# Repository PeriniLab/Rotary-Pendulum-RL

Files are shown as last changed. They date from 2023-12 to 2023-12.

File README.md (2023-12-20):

# Rotary-Pendulum-RL







https://github.com/PeriniM/Rotary-Pendulum-RL/assets/19621159/0168d43d-66d2-4de8-862b-840ff1d75a66

<!-- ![Rotary Pendulum](docs/assets/rotary_pybullet.jpg) -->
This is an open source project aimed at introducing people to **robotics**, from the hardware and embedded systems implementation to the software and control algorithms. The goal is to control a real life **rotary pendulum** to make it perform a swing-up and balance task.

The project is divided into four parts: **hardware**, **firmware**, **simulation** and **control**. The hardware part is responsible for the mechanical design and the electronic components. The firmware part is responsible for the embedded systems implementation. The simulation part is responsible for the simulation of the rotary pendulum in a virtual environment. The control part is responsible for the implementation of the control algorithms.

## [Documentation](https://rotary-pendulum-rl.readthedocs.io/)

## Folder Structure

```bash
├─── hardware
│   ├─── 3d_models
│   ├─── BOM
│   ├─── schematics
│   └─── instructions
│
├─── firmware
│   ├─── arduino
│   └─── platformio
│
├─── simulation
│   ├─── urdf
│   ├─── pybullet
│   └─── gazebo
│
├─── control
│   ├─── pid
│   ├─── optimal_control
│   └─── reinforcement_learning
│
└─── docs
    └─── assets
```
### 📂[hardware](hardware)

This folder contains the mechanical design and the electronic schematics as well as the instructions on how to build the rotary pendulum.
It will guide you through the process of 3D printing the parts, choosing the right mechanical and electronic components and assembling the rotary pendulum.

### 📂[firmware](firmware)

This folder contains the microcontroller code that will run on the embedded systems of the rotary pendulum.
It will guide you through the process of setting up the development environment, compiling and uploading the code to the microcontroller.

### 📂[simulation](simulation)

This folder contains the simulation code that will run on the computer. It will simulate the rotary pendulum in a virtual environment, such as the [PyBullet](https://pybullet.org/wordpress/) or [Gazebo](http://gazebosim.org/) simulators.

### 📂[control](control)

This folder contains the control code that will run on the computer. It will implement the control algorithms that will be used to control the rotary pendulum, from model-free to model-based control algorithms.

## Contributing

Contributions are what make the open source community such an amazing place to learn, inspire, and create. Any contributions you make are **greatly appreciated**.

If you want to contribute to this project, please read the [CONTRIBUTING.md](CONTRIBUTING.md) file.

## License

Distributed under the **Apache License 2.0**. See [LICENSE](LICENSE) for more information.

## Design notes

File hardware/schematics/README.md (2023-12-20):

# Schematics

The schematics of the electronics are yet to be added to the repository. The following is the drawn schematic, the pin numbers represent the GPIO pins of the ESP32 and the ones used in the code.

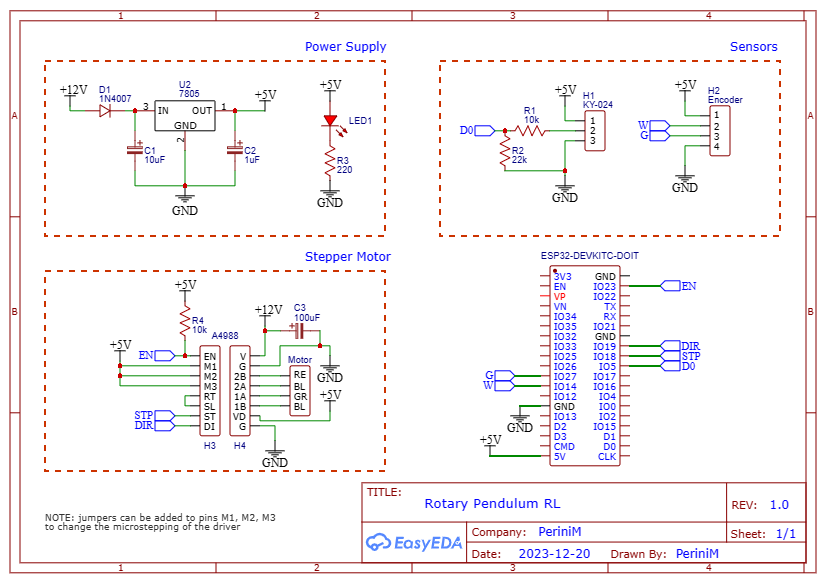
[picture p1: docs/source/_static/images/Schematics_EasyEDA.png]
Schematics


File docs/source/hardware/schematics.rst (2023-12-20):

.. _schematics:

Schematics
==========

The following is the electronics schematic to understand the connections.
Later on, a PCB will be designed.



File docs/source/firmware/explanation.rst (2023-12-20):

Example Firmware Explanation
----------------------------

The example firmware is split in three parts:

* `main.cpp` contains the main loop and the initialization code.
* `utils.cpp` contains some utility functions.
* `utils.h` contains the declarations of the utility functions.

utils.cpp
^^^^^^^^^

Here we define some utility functions that are used for handling the WiFi connection (right now it is not used) and 
for handling the pendulum rotation.
Expecially the function `getTheta` is important, since it maps the encoder counts to the angle of the pendulum.
The bar angle goes [-pi,pi] where zero is the upright position.

.. code-block:: c++

    #include <Arduino.h>
    #include <WiFi.h>
    #include <nvs_flash.h>

    bool connectToWiFi(const char* ssid, const char* password) {
    WiFi.begin(ssid, password);

    unsigned long startTime = millis();
    while (WiFi.status() != WL_CONNECTED && (millis() - startTime) < 2000) {
        delay(100);
        Serial.print(".");
    }

    if (WiFi.status() == WL_CONNECTED) {
        Serial.println("\nConnected to " + String(ssid));
        return true;
    } else {
        Serial.println("\nFailed to connect to " + String(ssid));
        WiFi.disconnect();
        return false;
    }
    }

    void setupWiFi(const char* ssids[], const char* passwords[], int NUM_NETWORKS) {
    if (nvs_flash_init() != ESP_OK) {
        Serial.println("Error initializing NVS");
        return;
    }

    nvs_handle my_handle;
    int32_t networkIndex = -1;

    if (nvs_open("storage", NVS_READONLY, &my_handle) == ESP_OK) {
        nvs_get_i32(my_handle, "networkIndex", &networkIndex);
        nvs_close(my_handle);
    }

    if (networkIndex >= 0 && networkIndex < NUM_NETWORKS) {
        if (connectToWiFi(ssids[networkIndex], passwords[networkIndex])) {
        return;
        }
    }

    for (int i = 0; i < NUM_NETWORKS; i++) {
        if (connectToWiFi(ssids[i], passwords[i])) {
        if (nvs_open("storage", NVS_READWRITE, &my_handle) == ESP_OK) {
            nvs_set_i32(my_handle, "networkIndex", i);
            nvs_commit(my_handle);
            nvs_close(my_handle);
        }
        break;
        }
    }
    }

    double getTheta(long encoderPosition, long encoderSteps) {
    double theta = 0.0;
    long half_revolutions = encoderPosition/encoderSteps; 
    if (encoderPosition > 0) {
        if (half_revolutions > 1 && half_revolutions % 2 == 0){
        theta = map(encoderPosition, half_revolutions * encoderSteps, (half_revolutions + 1)*encoderSteps, 31415,0) / 1e4;
        }
        else if (half_revolutions > 1 && half_revolutions % 2 == 1){
        theta = map(encoderPosition, half_revolutions * encoderSteps, (half_revolutions + 1)*encoderSteps, 0, -31415) / 1e4;
        }
        else {
        theta = map(encoderPosition, 0, encoderSteps, 31415, 0) / 1e4;
        }
    }
    else { 
        if (half_revolutions < -1 && half_revolutions % 2 == 0){
        theta = map(encoderPosition, half_revolutions * encoderSteps, (half_revolutions - 1)*encoderSteps, -31415,0) / 1e4;
        }
        else if (half_revolutions < -1 && half_revolutions % 2 == -1){
        theta = map(encoderPosition, half_revolutions * encoderSteps, (half_revolutions - 1)*encoderSteps, 0, 31415) / 1e4;
        }
        else {
        theta = map(encoderPosition, 0, -encoderSteps, -31415, 0) / 1e4;
        }
    }
    return theta;
    }

    double clip(double n, double lower, double upper) {
    return max(lower, min(n, upper));
    }

utils.h
^^^^^^^

Here we declare the utility functions.

.. code-block:: c++

    void setupWiFi(const char* ssids[], const char* passwords[], int NUM_NETWORKS);
    double getTheta(long encoderPosition, long encoderSteps);
    double clip(double n, double lower, double upper);

    #pragma once

main.cpp
^^^^^^^^

.. code-block:: c++

    #include <ESP32Encoder.h>
    #include <Arduino.h>
    #include "utils.h"

    // Define the pins used by the sensors
    #define ENCODER_A 14
    #define ENCODER_B 27
    #define HALL_SENSOR 26

    // Define the pins used by the stepper driver
    #define STEP_PIN 18
    #define DIR_PIN 19
    #define ENABLE_PIN 23
    // 1ULL shifts 1 to the left by STEP_PIN positions
    #define STEP_BIT (1ULL << STEP_PIN)
    #define DIR_BIT  (1ULL << DIR_PIN)
    #define ENABLE_BIT (1ULL << ENABLE_PIN)
    #define HALL_BIT (1ULL << HALL_SENSOR)

    // Define the number of networks you have
    #define NUM_NETWORKS 3

    // Create a list of SSID and passwords
    const char* ssids[NUM_NETWORKS] = {"FASTWEB-FC20AB", "ees-lab", "CasaCamilla_3"};
    const char* passwords[NUM_NETWORKS] = {"PP2NEEGH67", "cipiacelafft", "GranseolaCheSiole9102"};

    const long encoderSteps = 1200; // Encoder steps per half rotation
    ESP32Encoder encoder(true, NULL, NULL);

    const int steps_per_rev = 3200;
    // steps per second
    double maxSpeed = 4000.0; // Max speed in steps per second
    volatile double currentAngle = 0.0; // Current angle of the motor in degrees
    volatile double rangeAngle = 200.0; // Range of motion of the motor in degrees
    volatile const double degreesPerStep = 360.0 / steps_per_rev;
    volatile double speed = 0.0;
    volatile double homingSpeed = 2000.0;
    bool dir = false; // false = counter-clockwise, true = clockwise
    volatile long stepCount = 0;
    volatile bool homing = false;
    volatile bool episodeDone = false;
    volatile int hallSensorDebounce = 0;
    volatile bool hallSensorCentering = false;
    // millis variables for timing
    double timestep = 5.0; // ms
    double theta_dot = 0.0;
    double oldTheta = 0.0;
    unsigned long oldTime = 0.0;

    hw_timer_t *timer = NULL;
    portMUX_TYPE timerMux = portMUX_INITIALIZER_UNLOCKED;

    void sendSerialOutput(double angle, double angularVelocity, double currentAngle, bool episodeDone) {
    // Format the output string
    String output = String(angle) + "," + String(angularVelocity) + "," + String(currentAngle) + "," + String(episodeDone);
    Serial.println(output);
    }

    // Function to set direction
    void setDirection(bool direction) {
    dir = direction;
    if (dir) {
        GPIO.out |= DIR_BIT; // Set direction pin to HIGH
    } else {
        GPIO.out &= ~DIR_BIT; // Set direction pin to LOW
    }
    }

    // Function to set speed
    void setSpeed(double newSpeed) {
    if ((int)newSpeed == 0) {
        portENTER_CRITICAL(&timerMux);
        speed = newSpeed;
        timerAlarmDisable(timer);  // Disable the timer
        portEXIT_CRITICAL(&timerMux);
        // STEP pin to LOW to ensure the motor is not in mid-step
        GPIO.out &= ~STEP_BIT;
    } else {
        portENTER_CRITICAL(&timerMux);
        speed = newSpeed;
        timerAlarmWrite(timer, 1000000 / speed, true); // Update the timer interval
        timerAlarmEnable(timer);  // Re-enable the timer
        portEXIT_CRITICAL(&timerMux);
    }
    }

    // Function to zero the position
    void zeroPosition() {
    portENTER_CRITICAL(&timerMux);
    stepCount = 0; // Reset step count
    portEXIT_CRITICAL(&timerMux);
    }

    // Function to set speed based on percentage
    void setSpeedPercentage(int percentage) {
    speed = maxSpeed * (percentage / 100.0);
    setSpeed(speed);
    }

    // Function to move to home position
    void moveToHome() {
    homing = true;
    if (currentAngle > 0.0) {
        dir = false;
    }
    else if (currentAngle < 0.0) {
        dir = true;
    }
    else {
        homing = false;
        episodeDone = false;
        zeroPosition();
        setSpeed(0);
        return;
    }
    setDirection(dir);
    setSpeed(homingSpeed);
    }

    void IRAM_ATTR onTimer() {
    // If the speed is set to zero, exit the ISR without toggling the STEP pin
    if ((int)speed == 0) {
        return;
    }
    portENTER_CRITICAL_ISR(&timerMux);
    
    // Toggle the step pin for moving the motor
    if (GPIO.out & STEP_BIT) {
        GPIO.out &= ~STEP_BIT; // Set step pin to LOW
    } else {
        GPIO.out |= STEP_BIT; // Set step pin to HIGH
    }

    if (GPIO.in & HALL_BIT) {
        zeroPosition();
    }

    // Change steps only when step pin goes HIGH
    if (GPIO.out & STEP_BIT) {
        // update the steps the motor has moved from the beginning
        stepCount += dir ? 1 : -1;
        // convert steps to degree angle
        currentAngle = stepCount * degreesPerStep;
        // if the pendulum is not homing
        if (!homing){
        // if it is not inside the permitted range, bring pendulum back to home position
        if ((currentAngle >= rangeAngle/2 && !episodeDone) || (currentAngle <= -rangeAngle/2 && !episodeDone)) {
            episodeDone = true;
            moveToHome();
        }
        else {
            episodeDone = false;
        }
        }
        // if it is homing
        else {
        // check if the hall sensor gets activated and reset the position and speed
        if (GPIO.in & HALL_BIT && !hallSensorCentering) {
            hallSensorCentering = true;
            hallSensorDebounce = 0;
        }
        else if (GPIO.in & HALL_BIT && hallSensorCentering) {
            hallSensorDebounce++;
        }
        else if (!(GPIO.in & HALL_BIT) && hallSensorCentering && hallSensorDebounce > 5) {
            hallSensorCentering = false;
            hallSensorDebounce = 0;
            homing = false;
            episodeDone = false;
            zeroPosition();
            setSpeed(0);
            
        }
        }
    }
    
    portEXIT_CRITICAL_ISR(&timerMux);
    }

    void setup() {
    pinMode(ENCODER_A, INPUT_PULLUP);
    pinMode(ENCODER_B, INPUT_PULLUP);
    pinMode(HALL_SENSOR, INPUT);
    pinMode(ENABLE_PIN, OUTPUT);
    pinMode(STEP_PIN, OUTPUT);
    pinMode(DIR_PIN, OUTPUT);
    digitalWrite(ENABLE_PIN, LOW);  // Enable the motor

    // Connect to WiFi
    setupWiFi(ssids, passwords, NUM_NETWORKS);

    // to get accurate readings, the encoder ISR should be serviced by a core
    ESP32Encoder::isrServiceCpuCore=1;
    encoder.attachFullQuad(ENCODER_A, ENCODER_B);
    encoder.clearCount();
    encoder.setFilter(1023);

    Serial.begin(115200);

    // Set up the timer
    timer = timerBegin(0, 80, true); // Timer 0, prescaler 80, counting up
    timerAttachInterrupt(timer, &onTimer, true); // Attach onTimer function
    timerAlarmEnable(timer); // Enable the timer
    }

    void loop() {
    // get encoder count
    long currentCount = encoder.getCount();
    // map it in range [-3.14, 3.14]
    double theta = getTheta(currentCount, encoderSteps);

    // Check for incoming serial data if episode is not done
    if (Serial.available() > 0 && !episodeDone) {
        String command = Serial.readStringUntil('\n'); // Read the incoming data until newline
        command.trim(); // Remove any whitespace

        // Parse the command and execute it
        if (command.length() > 0) {
        // parse the command, for example "-20,0" to set the speed
        int commaIndex = command.indexOf(',');
        if (commaIndex != -1) {
            String speedStr = command.substring(0, commaIndex);
            String episodeStr = command.substring(commaIndex + 1);

            // clip speed percentage to [-100, 100]
            int speedPercentage = clip(speedStr.toInt(), -100, 100);
            bool episode = episodeStr.toInt(); // Convert episode to boolean (0 or 1)

            // if episode is not done
            if (!episode) {
            // Update speed and direction based on the command
            if (speedPercentage < 0) {
                dir = false;
                setDirection(dir); // Set direction counterclockwise
                speedPercentage = -speedPercentage; // Make the percentage positive
            } else if (speedPercentage > 0) {
                dir = true;
                setDirection(dir); // Set direction clockwise
            }
            else {
                speedPercentage = 0;
            }

            setSpeedPercentage(speedPercentage); // Set speed as a percentage of max speed
            episodeDone = false;
            }
            else {
            // If episode is done, bring pendulum back to home position
            episodeDone = true;
            moveToHome();
            }
        }
        }
    }

    // send data to serial
    if (millis() - oldTime >= timestep) {
        theta_dot = (theta - oldTheta) / (timestep/1000.0);
        // clip theta_dot to [-10, 10]
        theta_dot = clip(theta_dot, -10.0, 10.0);
        sendSerialOutput(theta, theta_dot, currentAngle, episodeDone);
        oldTime = millis();
        oldTheta = theta;    
    }
    
    }

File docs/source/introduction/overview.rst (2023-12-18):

Overview
========

This is an open source project aimed at introducing people to **robotics**, from the hardware
and embedded systems implementation to the software and control algorithms.
The goal is to control a real life **rotary pendulum** to make it perform a swing-up and balance task.

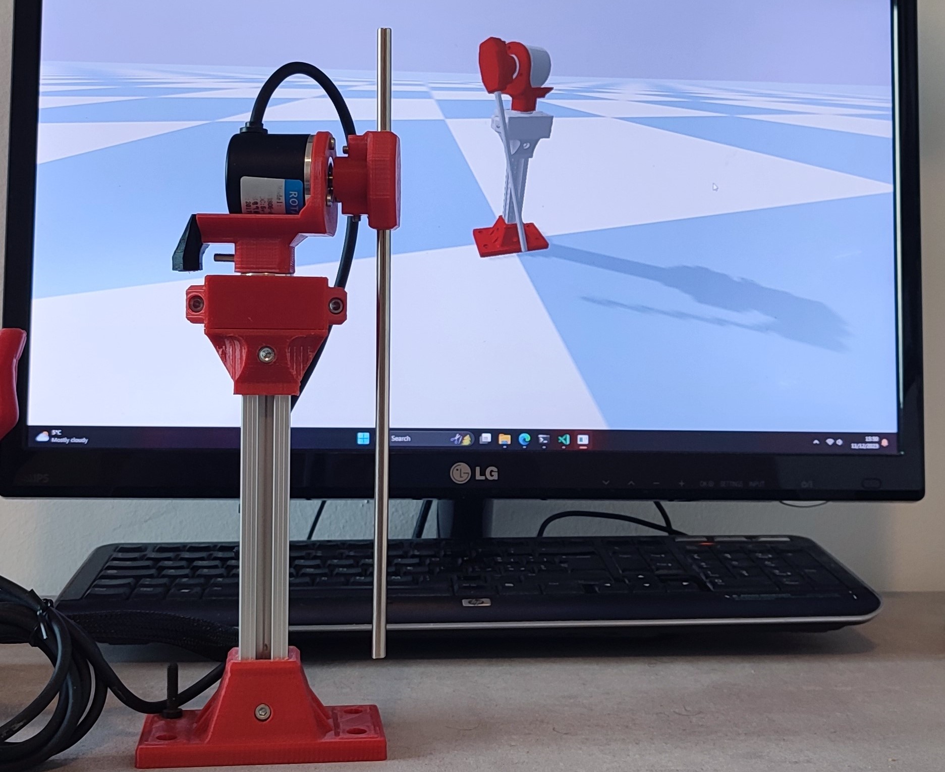
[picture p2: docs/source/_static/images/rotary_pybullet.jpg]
Rotary Pendulum


The project is divided into four parts: **hardware**, **firmware**, **simulation** and **control**.

- The **hardware** part is responsible for the mechanical design and the electronic components.
- The **firmware** part is responsible for the embedded systems implementation.
- The **simulation** part is responsible for the simulation of the rotary pendulum in a virtual environment.
- The **control part** is responsible for the implementation of the control algorithms.

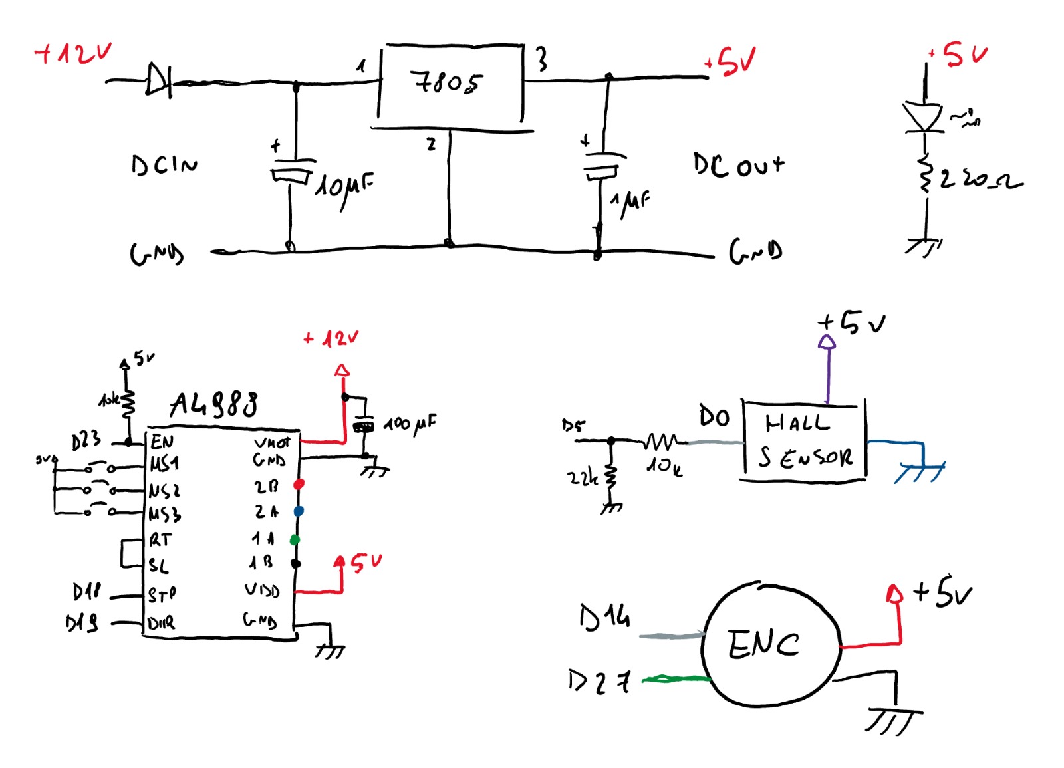
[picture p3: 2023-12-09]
docs/source/_static/images/drawn_schematics.jpg

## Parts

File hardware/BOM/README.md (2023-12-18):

# Bill of Materials

This directory contains the bill of materials for the hardware design of the Rotary Pendulum.

## Table of Contents

<!-- TOC depthFrom:2 depthTo:6 withLinks:1 updateOnSave:1 orderedList:0 -->

- [Bill of Materials](#bill-of-materials)
    - [Electronics](#electronics)
        - [Microcontroller](#microcontroller)
        - [Motor Driver](#motor-driver)
        - [Power Supply](#power-supply)
        - [Sensors](#sensors)
            - [Encoder](#encoder)
            - [Hall Effect Sensor](#hall-effect-sensor)
    - [Mechanical](#mechanical)
        - [Frame](#frame)
        - [3D Printed Parts](#3d-printed-parts)
        - [Motor](#motor)
        <!-- - [Miscellaneous](#miscellaneous) -->

<!-- /TOC -->

## Electronics

The following table lists the electronic components used in the design. You may use different components, but make sure that they are compatible with the design.

### Microcontroller

| Part Number | Description | Quantity | Price | Details |
|-------------|-------------|----------|-------|-----------|
| [ESP32-DevKit](https://docs.espressif.com/projects/esp-idf/en/latest/esp32/hw-reference/esp32/get-started-devkitc.html) | ESP32 Development Board | 1 | ~€10.00 | [Schematics](https://dl.espressif.com/dl/schematics/esp32_devkitc_v4-sch.pdf) |

### Motor Driver

| Part Number | Description | Quantity | Price | Details |
|-------------|-------------|----------|-------|---------|
| [A4988](https://www.pololu.com/product/1182) | Stepper Motor Driver | 1 | ~€3.00 | [Schematics](https://www.pololu.com/file/0J450/a4988_DMOS_microstepping_driver_with_translator.pdf) |

### Power Supply

The motor is powered using a 12V power supply. The ESP32 and other components are powered using a 5V power supply. The 5V power supply is generated using a step-down voltage regulator.

| Part Number | Description | Quantity | Price | Details |
|-------------|-------------|----------|-------|---------|
| [LM7805](https://www.sparkfun.com/datasheets/Components/LM7805.pdf) | 5V Voltage Regulator | 1 | ~€0.50 |  |

### Sensors

#### Encoder

An incremental rotary encoder is used to measure the bar angle. The encoder has 600 pulses per revolution and it is powered using 5V.

| Part Number | Description | Quantity | Price | Details |
|-------------|-------------|----------|-------|---------|
| [Rotary Encoder](https://www.fruugo.it/600p-r-encoder-di-rotazione-incrementale-magnetoelettrico-5v24v-ab-2fasi-albero-6mm/p-120440516-253131421?language=en) | 600 P/R Incremental Encoder | 1 | ~€20.00 | [Datasheet](datasheets/incremental_rotary_encoder_datasheet.pdf) |

#### Hall Effect Sensor

| Part Number | Description | Quantity | Price | Details |
|-------------|-------------|----------|-------|---------|
| [KY-024](https://arduinomodules.info/ky-024-linear-magnetic-hall-module/) | Linear Hall Effect Sensor | 1 | ~€1.00 | [Datasheet](datasheets/linear_magnetic_hall_sensor_datasheet.PDF) |

## Mechanical

### Frame

The frame is made out of an alluminium profile with a cross section of 20x20mm. The length of the profile is around 180mm.

You can use any other material with a different cross section, but make sure that the dimensions are compatible with the design and it is strong enough to sustain the stesses.

| Part Number | Description | Quantity | Price | Details |
|-------------|-------------|----------|-------|---------|
| [20x20mm Alluminium Profile](https://www.motedis.com/en/Aluminium-Profile-20x20-I-Typ-slot-5) | 20x20mm Alluminium Profile | 1 | ~€2.00 | [3D Model](https://www.thingiverse.com/thing:6324741) |

### 3D Printed Parts

You can find the 3D models of the parts in the [3d_models/stl](../3d_models/stl/) directory.
The parts were printed using PLA but you can use any other material (try avoiding rubber 😜).

I have also posted the models on Thingiverse and Cults3D:

- [Thingiverse](https://www.thingiverse.com/thing:6377165)
- [Cults3D](https://cults3d.com/en/3d-model/various/rotary-pendulum-rl-open-source-project)

### Motor

| Part Number | Description | Quantity | Price | Details |
|-------------|-------------|----------|-------|---------|
| [NEMA 17 Stepper Motor](https://www.omc-stepperonline.com/nema-17-high-temp-stepper-motor-16ncm-22-7oz-in-extruder-motor-insulation-class-h-180c-17hs08-1004s-h) | 17HS08-1004S | 1 | ~€10.00 | [Datasheet](datasheets/nema17-17HS08-1004S.pdf) |

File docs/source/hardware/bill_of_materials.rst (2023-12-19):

.. _bom:

Bill of Materials
=================

This directory contains the bill of materials for the hardware design of the Rotary Pendulum.

.. contents:: Table of Contents
   :local:
   :depth: 2

.. _electronics:

Electronics
^^^^^^^^^^^

Microcontroller
---------------

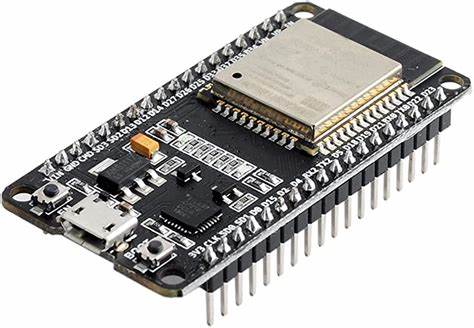
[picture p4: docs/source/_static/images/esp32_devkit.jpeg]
Esp32 DevKit


+--------------------------+--------------------------+----------+---------+--------------------------------------------------+
| Part Number              | Description              | Quantity | Price   | Details                                          |
+==========================+==========================+==========+=========+==================================================+
| `ESP32-DevKit`_          | ESP32 Development Board  | 1        | ~€10.00 | `EspSchematics`_                                 |
+--------------------------+--------------------------+----------+---------+--------------------------------------------------+

Motor Driver
------------

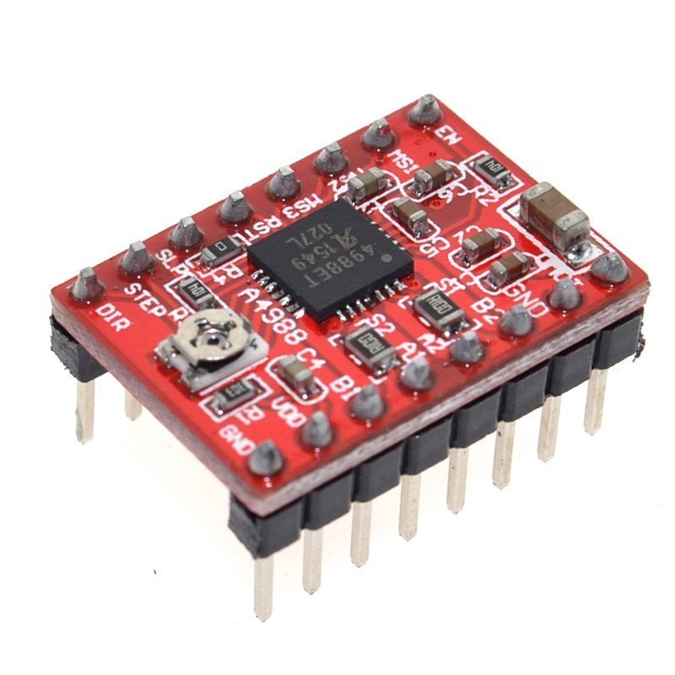
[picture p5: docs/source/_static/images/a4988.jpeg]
A4988


+--------------------------+---------------------+----------+--------+---------------------------------------------------+
| Part Number              | Description         | Quantity | Price  | Details                                           |
+==========================+=====================+==========+========+===================================================+
| `A4988`_                 | Stepper Motor Driver| 1        | ~€3.00 | `DriverSchematics`_                               |
+--------------------------+---------------------+----------+--------+---------------------------------------------------+

Power Supply
------------

The motor is powered using a 12V power supply. The ESP32 and other components are powered using a 5V power supply. The 5V power supply is generated using a step-down voltage regulator.

+--------------------------+---------------------+----------+--------+---------------------------------------------------+
| Part Number              | Description         | Quantity | Price  | Details                                           |
+==========================+=====================+==========+========+===================================================+
| `LM7805`_                | 5V Voltage Regulator| 1        | ~€0.50 |                                                   |
+--------------------------+---------------------+----------+--------+---------------------------------------------------+

Sensors
-------

Encoder
~~~~~~~

An incremental rotary encoder is used to measure the bar angle. The encoder has 600 pulses per revolution and it is powered using 5V.

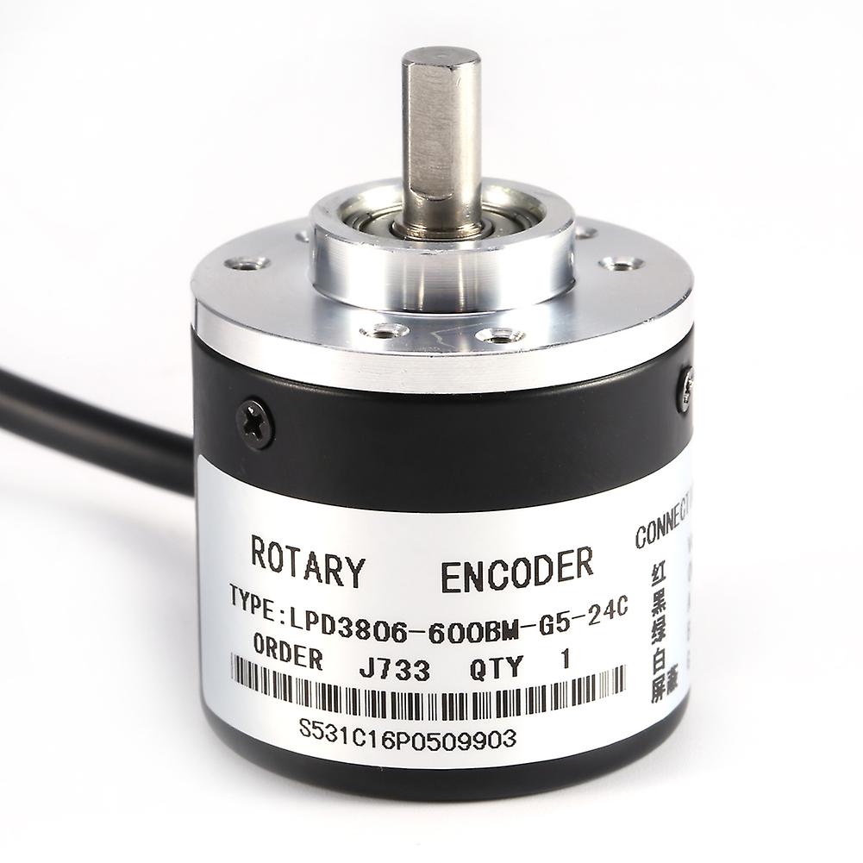
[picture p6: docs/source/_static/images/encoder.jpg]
Rotary Encoder


+--------------------------+-------------------------+----------+--------+----------------------------------------------------+
| Part Number              | Description             | Quantity | Price  | Details                                            |
+==========================+=========================+==========+========+====================================================+
| `Rotary Encoder`_        | 600 P/R Incremental     | 1        | ~€20.00| `RotaryDatasheet`_                                 |
|                          | Encoder                 |          |        |                                                    |
+--------------------------+-------------------------+----------+--------+----------------------------------------------------+

Hall Effect Sensor
~~~~~~~~~~~~~~~~~~

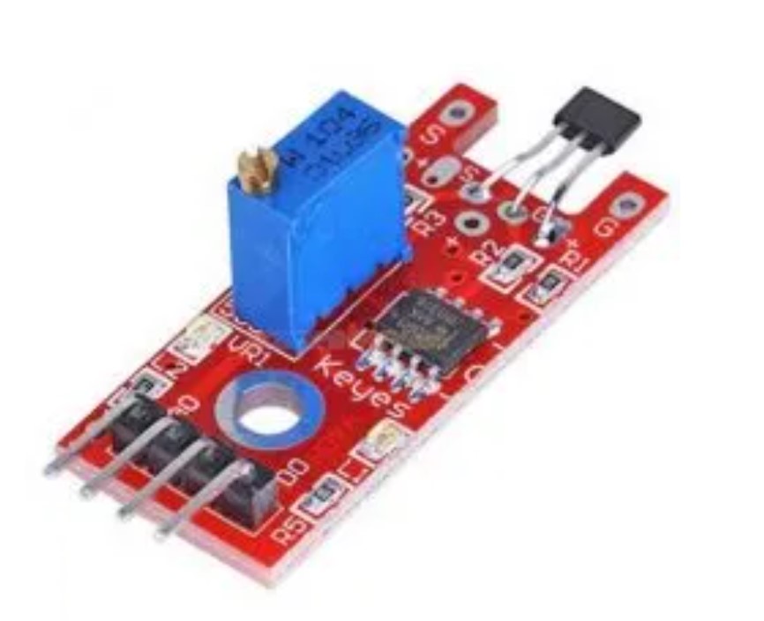
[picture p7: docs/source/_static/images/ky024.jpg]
Hall Effect Sensor


+--------------------------+-------------------------+----------+--------+---------------------------------------------------+
| Part Number              | Description             | Quantity | Price  | Details                                           |
+==========================+=========================+==========+========+===================================================+
| `KY-024`_                | Linear Hall Effect      | 1        | ~€1.00 | `HallDatasheet`_                                  |
|                          | Sensor                  |          |        |                                                   |
+--------------------------+-------------------------+----------+--------+---------------------------------------------------+

Mechanics
^^^^^^^^^

Frame
-----

The frame is made out of an alluminium profile with a cross section of 20x20mm. The length of the profile is around 180mm.

You can use any other material with a different cross section, but make sure that the dimensions are compatible with the design and it is strong enough to sustain the stresses.

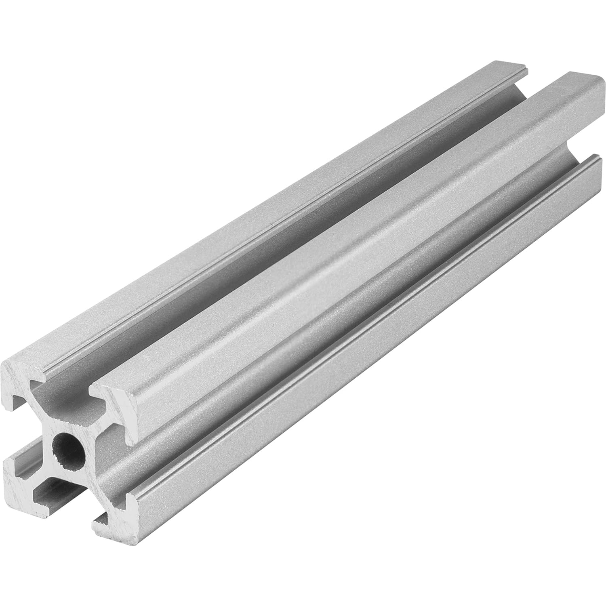
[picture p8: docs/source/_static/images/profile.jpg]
20x20mm Alluminium Profile


+--------------------------+---------------------+----------+--------+---------------------------------------------------+
| Part Number              | Description         | Quantity | Price  | Details                                           |
+==========================+=====================+==========+========+===================================================+
| `20x20mm Alluminium`_    | 20x20mm Alluminium  | 1        | ~€2.00 | `3D Model Profile`_                               |
|                          | Profile             |          |        |                                                   |
+--------------------------+---------------------+----------+--------+---------------------------------------------------+

3D Printed Parts
~~~~~~~~~~~~~~~~

You can find the 3D models of the parts in the :ref:`3d_models` section.
The parts were printed using PLA but you can use any other material (try avoiding rubber 😜).

I have also posted the models on Thingiverse and Cults3D:

- `Thingiverse`_
- `Cults3D`_

Motor
-----

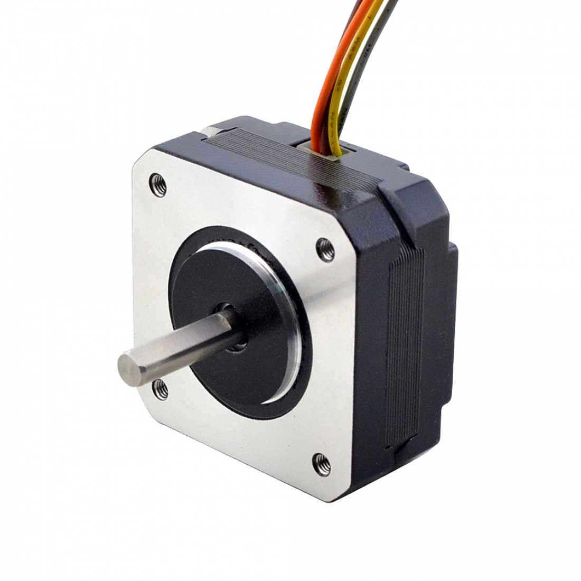
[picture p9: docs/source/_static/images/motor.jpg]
NEMA 17 Stepper Motor


+--------------------------+-------------------------+----------+--------+---------------------------------------------------+
| Part Number              | Description             | Quantity | Price  | Details                                           |
+==========================+=========================+==========+========+===================================================+
| `NEMA 17 Stepper Motor`_ | 17HS08-1004S            | 1        | ~€10.00| `MotorDatasheet`_                                 |
+--------------------------+-------------------------+----------+--------+---------------------------------------------------+

.. _ESP32-DevKit: https://docs.espressif.com/projects/esp-idf/en/latest/esp32/hw-reference/esp32/get-started-devkitc.html
.. _EspSchematics: https://dl.espressif.com/dl/schematics/esp32_devkitc_v4-sch.pdf
.. _A4988: https://www.pololu.com/product/1182
.. _DriverSchematics: https://www.pololu.com/file/0J450/a4988_DMOS_microstepping_driver_with_translator.pdf
.. _LM7805: https://www.sparkfun.com/datasheets/Components/LM7805.pdf
.. _Rotary Encoder: https://www.fruugo.it/600p-r-encoder-di-rotazione-incrementale-magnetoelettrico-5v24v-ab-2fasi-albero-6mm/p-120440516-253131421?language=en
.. _RotaryDatasheet: https://github.com/PeriniM/Rotary-Pendulum-RL/blob/main/hardware/BOM/datasheets/incremental_rotary_encoder_datasheet.pdf
.. _KY-024: https://arduinomodules.info/ky-024-linear-magnetic-hall-module/
.. _HallDatasheet: https://github.com/PeriniM/Rotary-Pendulum-RL/blob/main/hardware/BOM/datasheets/linear_magnetic_hall_sensor_datasheet.PDF
.. _20x20mm Alluminium: https://www.motedis.com/en/Aluminium-Profile-20x20-I-Typ-slot-5
.. _3D Model Profile: https://www.thingiverse.com/thing:6324741
.. _Thingiverse: https://www.thingiverse.com/thing:6377165
.. _Cults3D: https://cults3d.com/en/3d-model/various/rotary-pendulum-rl-open-source-project
.. _NEMA 17 Stepper Motor: https://www.omc-stepperonline.com/nema-17-high-temp-stepper-motor-16ncm-22-7oz-in-extruder-motor-insulation-class-h-180c-17hs08-1004s-h
.. _MotorDatasheet: https://github.com/PeriniM/Rotary-Pendulum-RL/blob/main/hardware/BOM/datasheets/nema17-17HS08-1004S.pdf

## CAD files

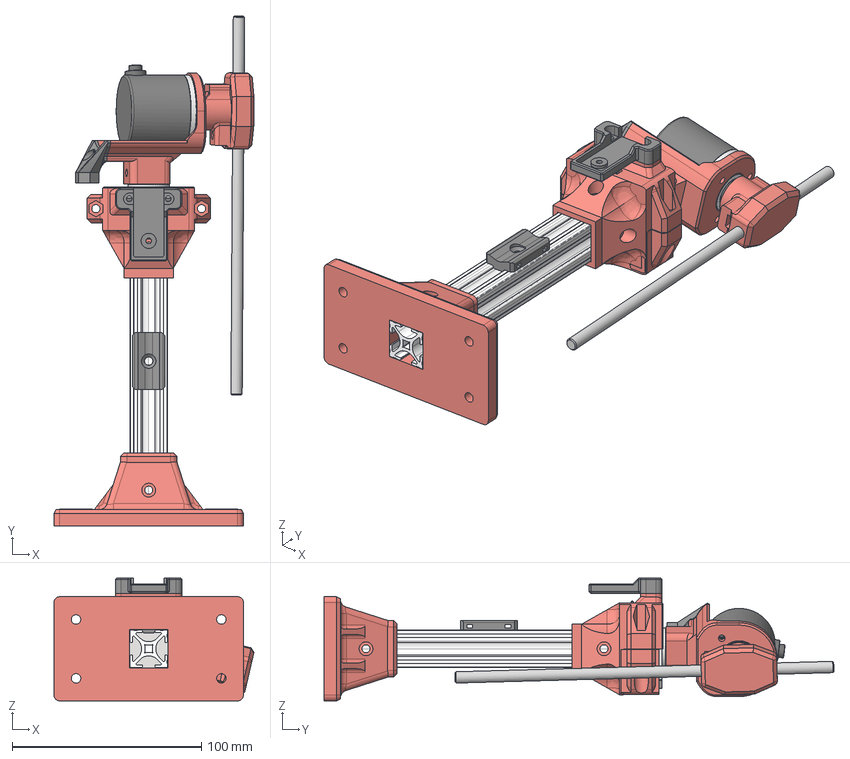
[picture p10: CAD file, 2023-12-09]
hardware/3d_models/Rotary_Pendulum_Assembly.step
105.6 x 269.2 x 64.8 mm
base_link
20x20_Alluminum_Bar
Stepper_Clamp_base
Stepper_NEMA_17
Stepper_Clamp_Top
Encoder_Support
Rotary_Encoder
Magnet_Support
8x2_Magnet
Hall_Sensor_Support
Cables_Holder
Holder_Bar_Cylinder
Steel_Bar_6mm

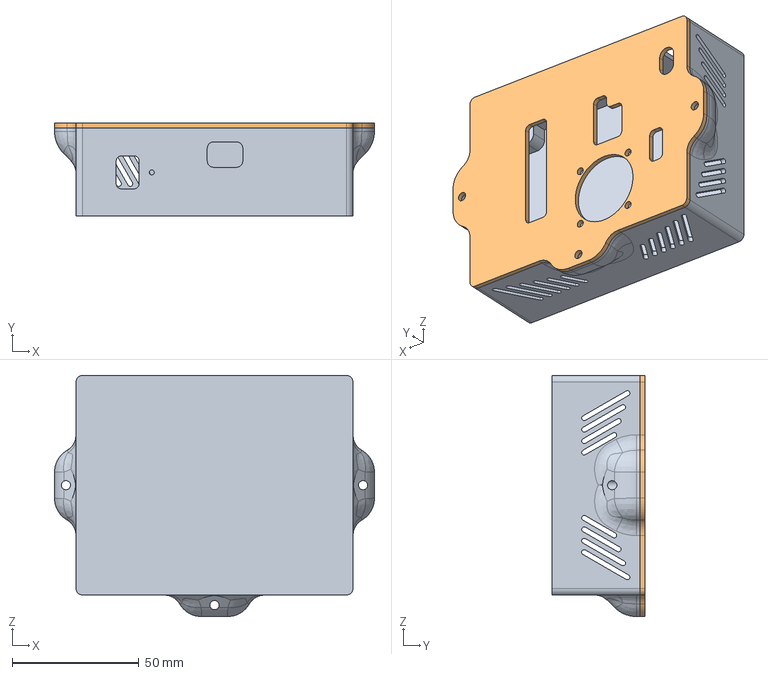
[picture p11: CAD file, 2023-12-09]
hardware/3d_models/PCB_Case_Assembly.step
126.0 x 36.8 x 94.9 mm

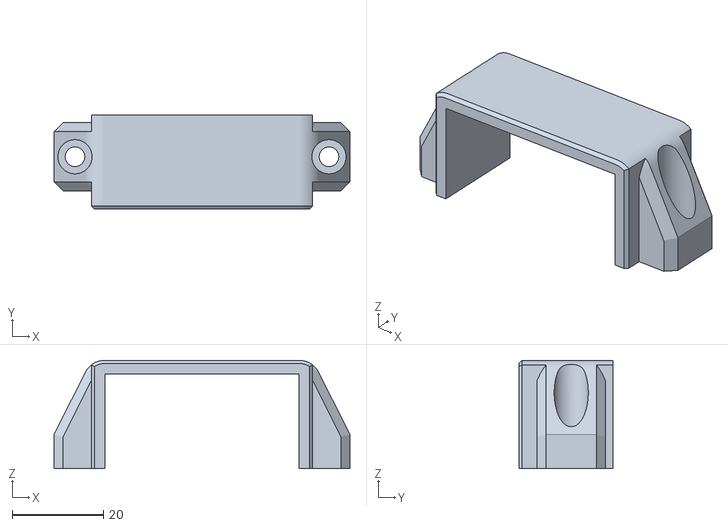
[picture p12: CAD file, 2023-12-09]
hardware/3d_models/stl/stepper_clamp_top.stl
65.0 x 20.7 x 23.8

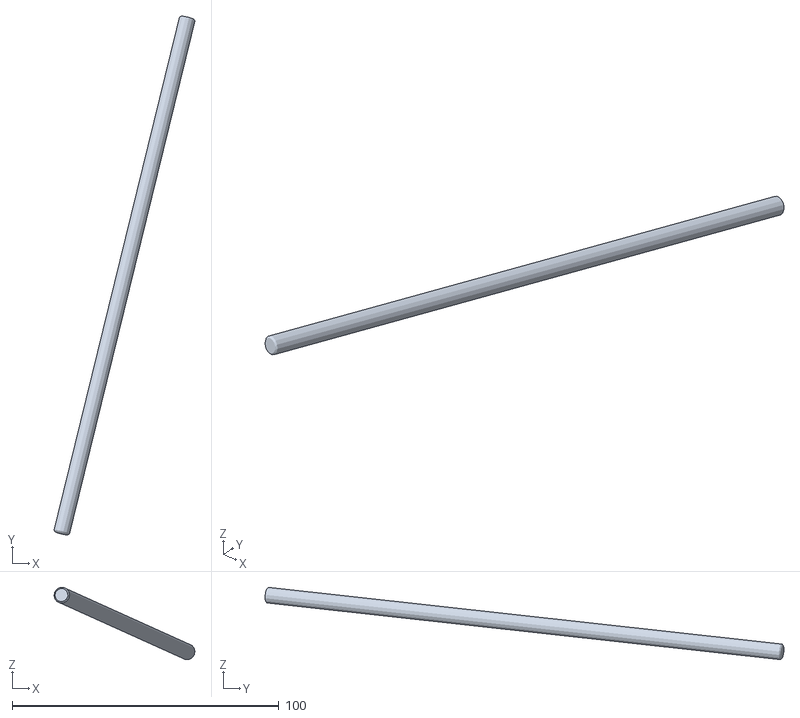
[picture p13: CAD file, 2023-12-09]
simulation/urdf/meshes/Steel_Bar_6mm_v31.stl
52.8 x 194.4 x 27.1

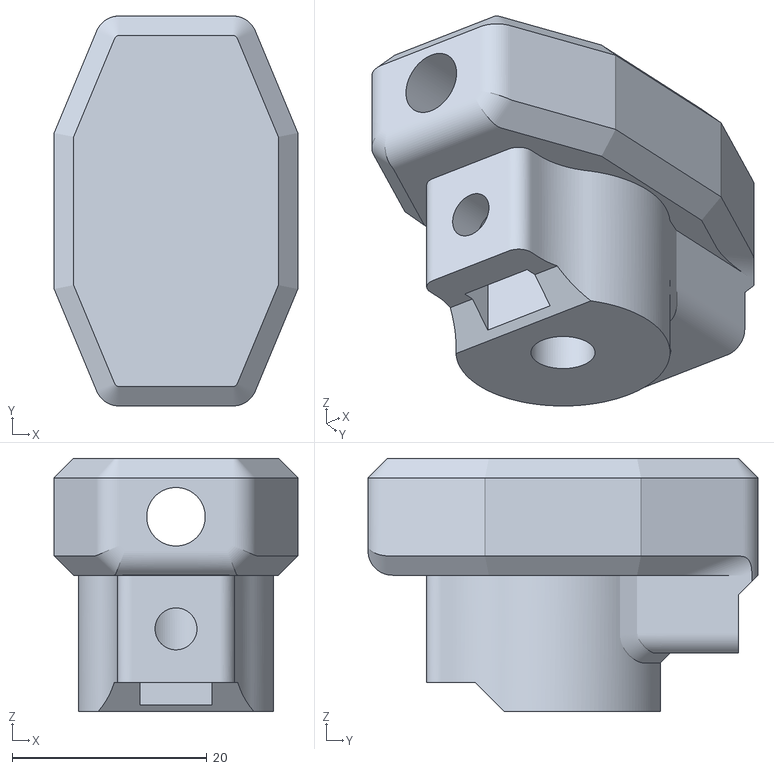
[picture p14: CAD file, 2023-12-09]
hardware/3d_models/stl/holder_bar_cylinder.stl
25.0 x 40.0 x 26.0

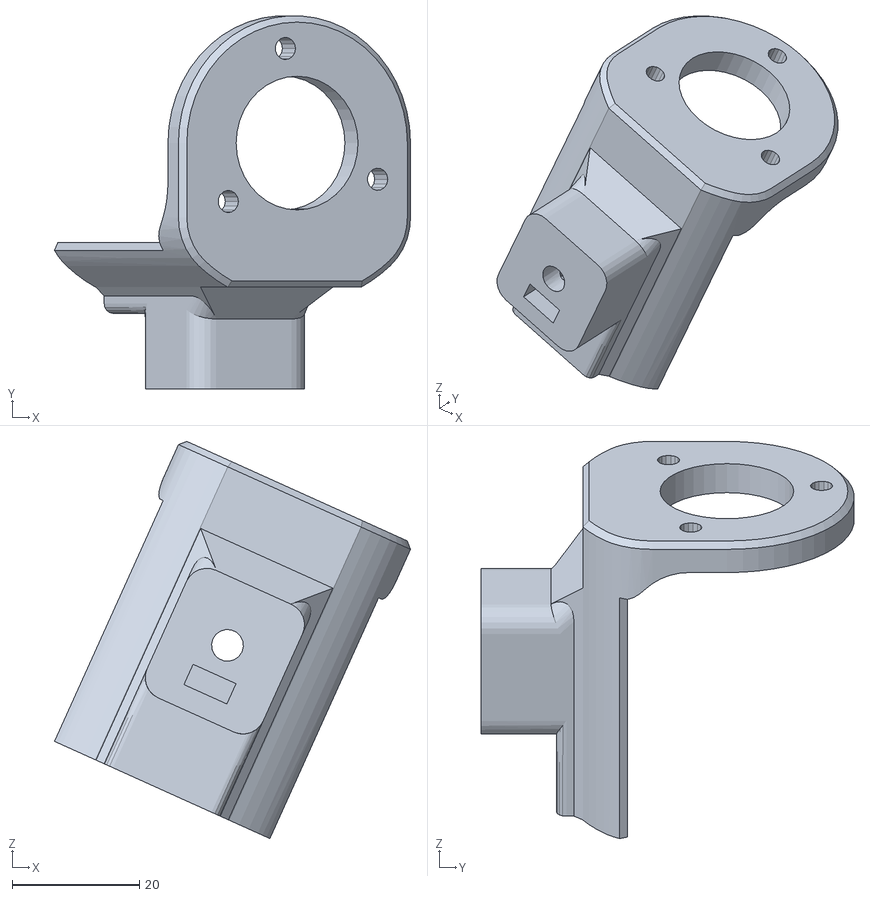
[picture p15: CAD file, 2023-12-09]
simulation/urdf/meshes/Encoder_Support_v41.stl
55.9 x 58.6 x 62.4

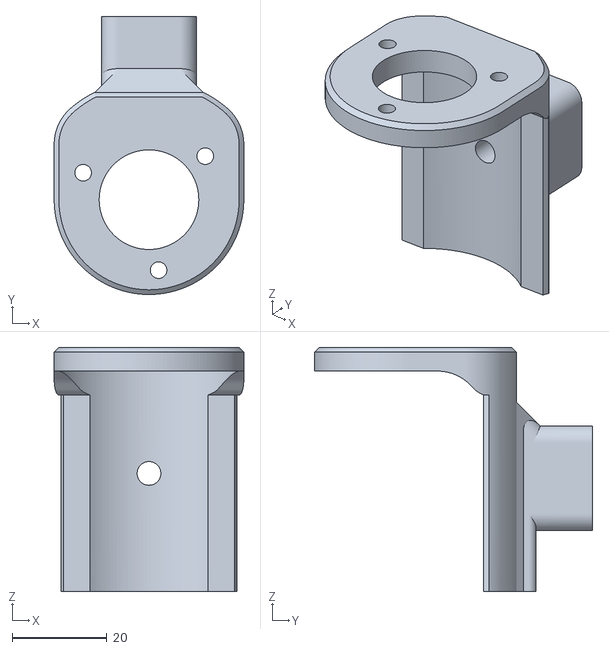
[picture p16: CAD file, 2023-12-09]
hardware/3d_models/stl/encoder_support.stl
40.0 x 58.6 x 51.5

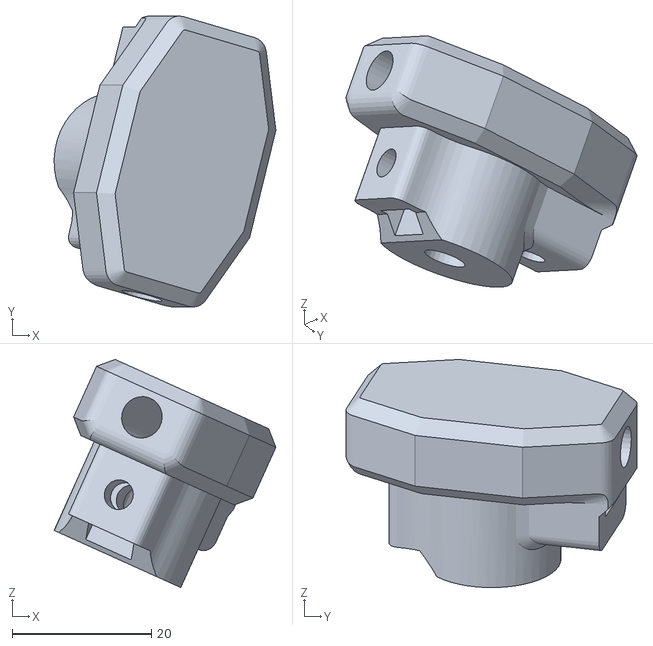
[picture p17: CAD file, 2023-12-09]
simulation/urdf/meshes/Holder_Bar_Cylinder_v31.stl
31.9 x 41.8 x 32.8

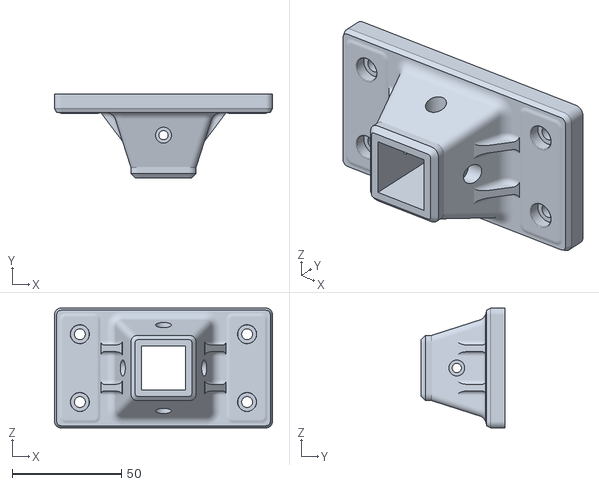
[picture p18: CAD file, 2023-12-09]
hardware/3d_models/stl/base_link.stl
100.0 x 38.6 x 55.0

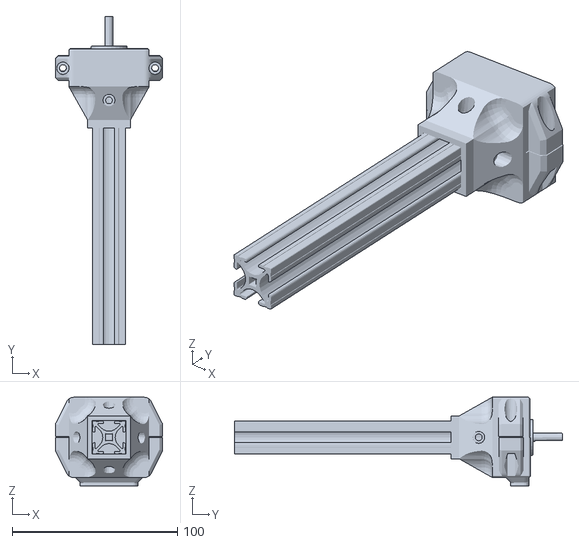
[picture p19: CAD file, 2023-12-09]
simulation/urdf/meshes/turret1.stl
65.0 x 198.5 x 53.6

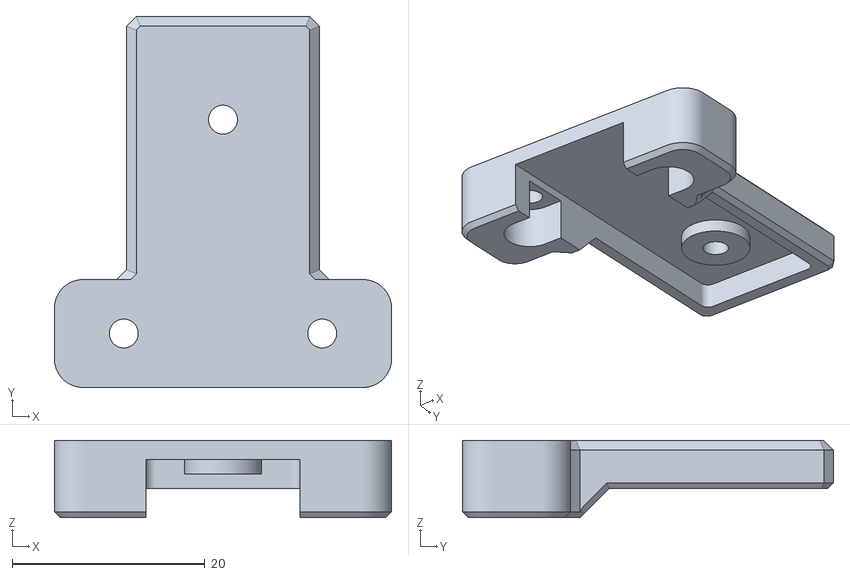
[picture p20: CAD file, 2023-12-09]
hardware/3d_models/stl/hall_sensor_support.stl
35.0 x 38.5 x 8.00

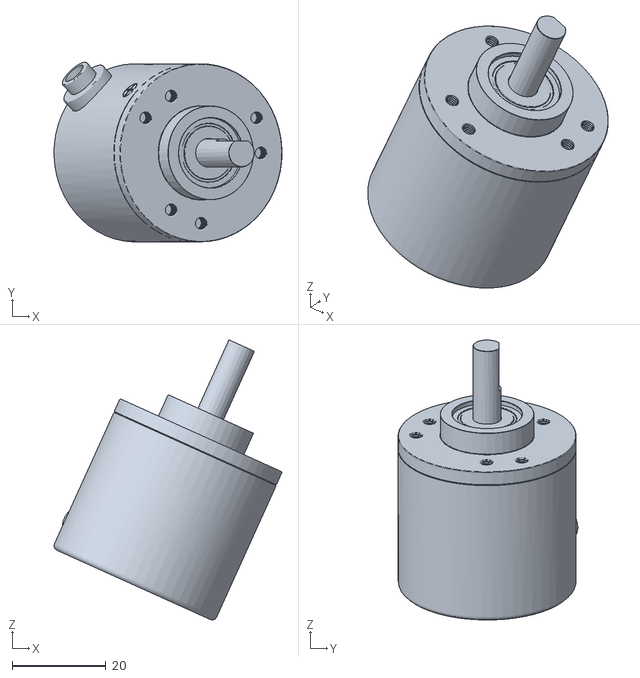
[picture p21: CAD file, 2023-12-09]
simulation/urdf/meshes/Encoder_v51.stl
48.6 x 38.3 x 59.7

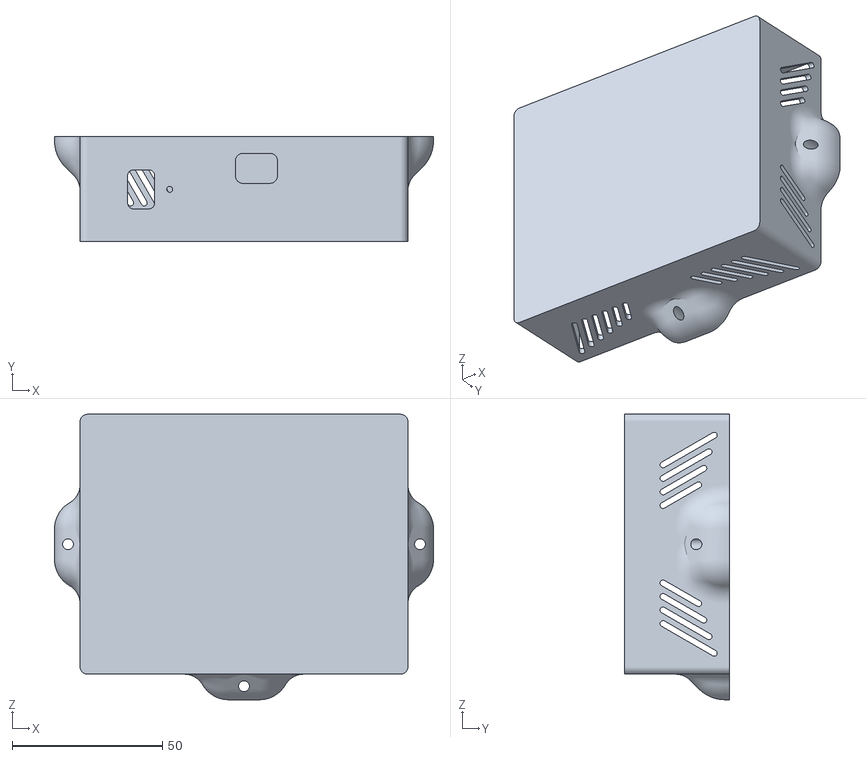
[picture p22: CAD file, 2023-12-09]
hardware/3d_models/stl/PCB_case_bottom.stl
126.0 x 34.8 x 94.9

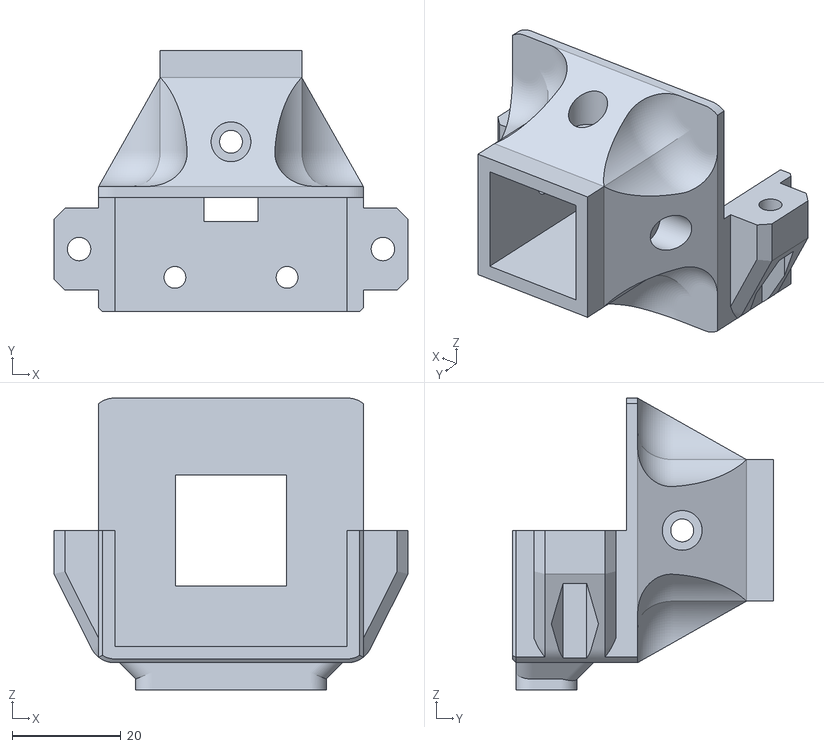
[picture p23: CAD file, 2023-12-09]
hardware/3d_models/stl/stepper_clamp_base.stl
65.0 x 48.0 x 53.6

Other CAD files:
simulation/urdf/meshes/base_link.stl
hardware/3d_models/stl/cables_holder.stl
hardware/3d_models/stl/magnet_support.stl

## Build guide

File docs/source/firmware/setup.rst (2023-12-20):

.. _firmware_setup:

Set-up
------

In order to be able to develop the microcontroller firmware and flash it to the board, you will need to install some dependencies.

USB-to-serial Driver
^^^^^^^^^^^^^^^^^^^^

When using the ESP32 Devkit board, you will need to install the USB-to-serial driver for the CP210x chip.
You can find the driver for your operating system on the `Silicon Labs website <https://www.silabs.com/developers/usb-to-uart-bridge-vcp-drivers?tab=downloads>`_.
In this way, you will be able to flash the firmware to the board and see the debug messages.

.. note::
    If you are using a different board, you will need to install the USB-to-serial driver for the chip on your board.
    Another common chip is the CH340x.

PlatformIO
^^^^^^^^^^

The firmware is developed using PlatformIO, which is an open source ecosystem for IoT development.
It supports more than 600 development boards and 20 development platforms, including the ESP32 Devkit-Doit-V1.

You can install PlatformIO using the `official documentation <https://docs.platformio.org/en/latest/integration/ide/vscode.html#ide-vscode>`_,
which basically consists in installing the PlatformIO extension for Visual Studio Code.

.. note::
    If you want to get started with an already configured project, you can import the existing pendulum firmware which can be found in the 
    `Github repo <https://github.com/PeriniM/Rotary-Pendulum-RL/tree/main/firmware>`_.

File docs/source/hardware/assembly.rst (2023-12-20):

.. _assembly:

Assembly
========

Here you can see how the assembly of the pendulum is done.

.. warning::

   Screws and bolts are not shown in the animation.

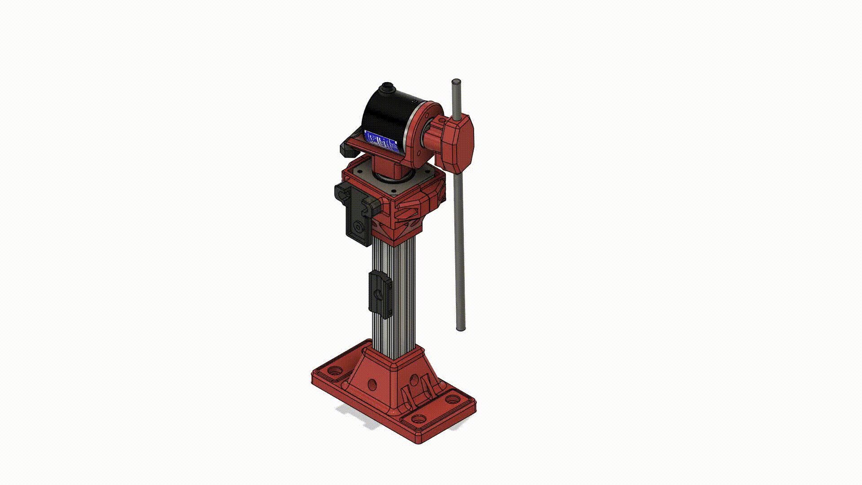
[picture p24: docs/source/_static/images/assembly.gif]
Assembly GIF


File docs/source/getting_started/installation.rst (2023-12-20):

Installation
------------

In the following sections I will guide you through the installation process of the required components
for this project. From the python dependencies (for running the simulation and controlling the robot)
to the set-up of the microcontroller firmware development.

If you would like to jump straight to the building and assembling of the robot and then come back later,
you can do so by skipping to the :ref:`bill of materials <bom>` section.

Prerequisites
^^^^^^^^^^^^^

- `Python 3.8+ <https://www.python.org/downloads/>`_
- `Git <https://git-scm.com/downloads>`_
- `Arduino IDE <https://www.arduino.cc/en/software>`_ or `PlatformIO <https://platformio.org/install/ide?install=vscode>`_
- `Visual Studio Code <https://code.visualstudio.com/download>`_ or IDE of your choice

External dependencies
^^^^^^^^^^^^^^^^^^^^^

Windows
+++++++

If you plan to simulate the rotary pendulum on your PC, for example using PyBullet, you will need to install `Build Tools for Visual Studio 2022 <https://aka.ms/vs/17/release/vs_BuildTools.exe>`_. Make sure to select the **C++ build tools** option.

You can as well install them in one go using `winget <https://docs.microsoft.com/en-us/windows/package-manager/winget/>`_ in the command line:

.. code-block:: bash

   # Windows 10 SDK
   winget install Microsoft.VisualStudio.2022.BuildTools --force --override "--wait --passive --add Microsoft.VisualStudio.Component.VC.Tools.x86.x64 --add Microsoft.VisualStudio.Component.Windows10SDK"

   # Windows 11 SDK
   winget install Microsoft.VisualStudio.2022.BuildTools --force --override "--wait --passive --add Microsoft.VisualStudio.Component.VC.Tools.x86.x64 --add Microsoft.VisualStudio.Component.Windows11SDK.22000"

Linux
++++++

You don't need to install any external dependencies.

Clone the repository
^^^^^^^^^^^^^^^^^^^^

.. code-block:: bash

   git clone https://github.com/PeriniM/Rotary-Pendulum-RL.git
   cd Rotary-Pendulum-RL

Create a virtual environment
^^^^^^^^^^^^^^^^^^^^^^^^^^^^

It is recommended to create a virtual environment to install the dependencies in order to avoid conflicts with other projects.

.. code-block:: bash

   python -m venv venv
   # python3 -m venv venv

Activate the virtual environment
^^^^^^^^^^^^^^^^^^^^^^^^^^^^^^^^

All the commands must be executed in the virtual environment. If you are not familiar with virtual environments, please read the `Python Virtual Environments: A Primer <https://realpython.com/python-virtual-environments-a-primer/>`_ article.

To activate the virtual environment, run the following command:

.. code-block:: bash

   # Windows
   .\venv\Scripts\activate
   # Linux
   source venv/bin/activate

Install the dependencies
^^^^^^^^^^^^^^^^^^^^^^^^

In the **requirements.txt** file you will find all the dependencies needed to run the code. To install them, run the following command:

.. code-block:: bash

   pip install -r requirements.txt
   # pip3 install -r requirements.txt

If you plan to implement some reinforcement learning algorithms, especially using `Stable Baselines 3 <https://stable-baselines.readthedocs.io/en/master/>`_, you will need to install the Pytorch dependencies.
Go to the `Pytorch website <https://pytorch.org/>`_, fill the installation wizard and run the command that will be provided to you. In this way you can opt to use the GPU or not.
An example of the command is the following:

.. code-block:: bash

   pip3 install torch torchvision torchaudio --index-url https://download.pytorch.org/whl/cu118

Test the installation
^^^^^^^^^^^^^^^^^^^^^

- Let's test if the pybullet installation was successful. Run the following command:

    .. code-block:: bash

       python ./simulation/pybullet/main.py
       # python3 ./simulation/pybullet/main.py

- Let's test if the modules works. Run the following command:

    .. code-block:: bash

       python -m control.reinforcement_learning.src.main
       # or
       python -m control.pid.src.main

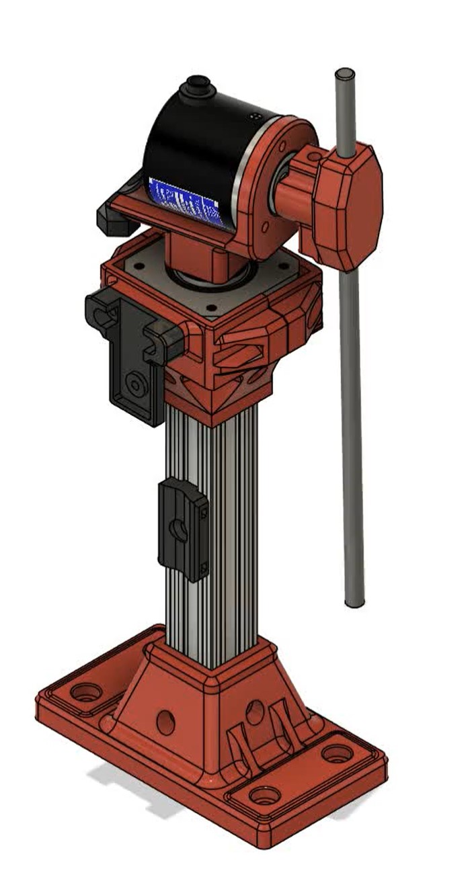
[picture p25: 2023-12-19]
docs/source/_static/images/full_assembly.jpg

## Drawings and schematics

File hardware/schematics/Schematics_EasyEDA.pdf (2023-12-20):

## GND

Power Supply | Sensors

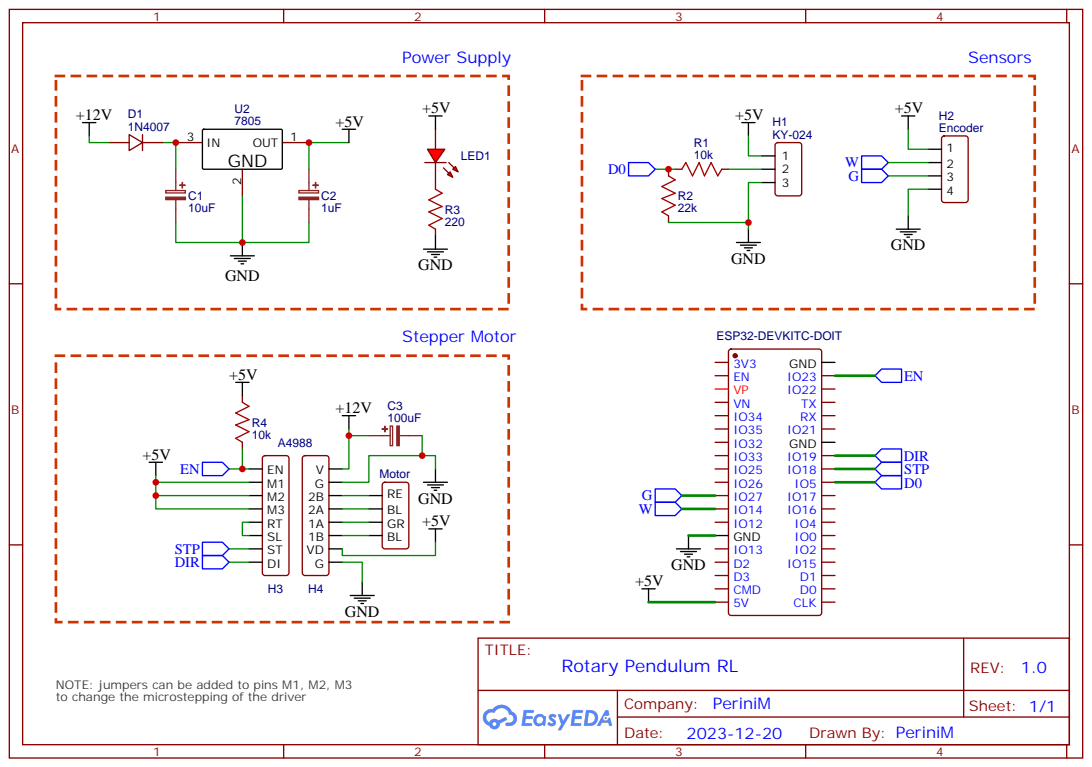
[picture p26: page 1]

NOTE: jumpers can be added to pins M1, M2, M3
to change the microstepping of the driver

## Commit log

2023-12-09 ADD first commit
    [Encoder_Support_v41.stl, Encoder_v51.stl, Holder_Bar_Cylinder_v31.stl, PCB_Case_Assembly.step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]
2023-12-15 dev: added assembly video
